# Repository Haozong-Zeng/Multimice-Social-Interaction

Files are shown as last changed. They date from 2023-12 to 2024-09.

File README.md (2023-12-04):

# Multimice-Social-Interaction
This repository contains the codes and documents of the multiple mice social interaction project in Dr. Tim Murphy's Lab at UBC.  
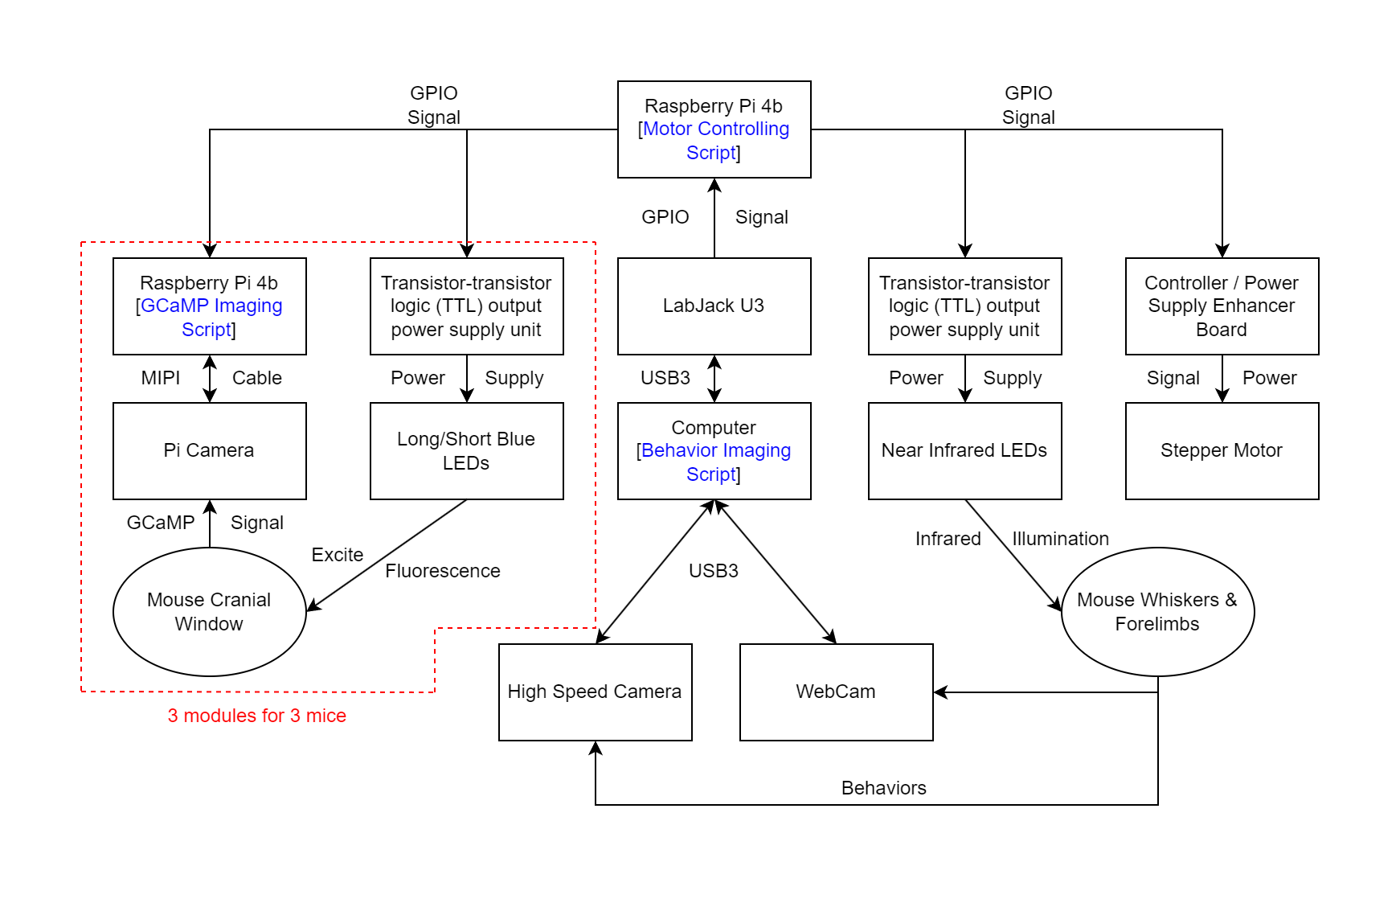
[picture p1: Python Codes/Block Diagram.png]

## Python Codes
This folder contains the python codes for 1) using Raspberry Pi to control the rail system and Pi cameras; 2) controlling the high-speed camera; 3) processing the obtained data. There is also a block diagram explaining how the system works.  
## Hardwares
This folder contains 1) a table with all of the parts; 2) CAD files for the customized parts made by 3D printing or CNC; 3) assembly diagrams to show how the rig is constructed.

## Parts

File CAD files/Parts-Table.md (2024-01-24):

# Parts Required for Constructing the Rig
This table contains a list of parts required to build the experimental setup. These parts are divided into those that can be purchased and those that need to be customized. Customized parts can be obtained by simply providing CAD files to 3D printing and CNC manufacturers, and the processing costs are not high.  
## Parts to be purchased
**1**. 4 Raspberry Pi 4b - Connecting to Pi cameras for brain imaging; GPIO for synchronization, controlling the stepper motor & LEDs. Other versions of Raspberry Pi might require extra modification.  
**2**. 1 LabJack LabJack U3-LV - Connection to a computer with the high-speed camera (OMRON STC-MBS43U3V) to provide GPIO for synchronization.  
**3**. 1 OMRON STC-MBS43U3V camera - Recording whisker movements at high fps.  
**4**. 1 Full-band Beam Splitter (Reflection/Transmission Ratio 80%/20%) from Edmund Optics - Recording whisker & limbs.  
**5**. 1 Computer - Recording behavior data at high fps.  
**6**. 3 Raspberry Pi Cameras (OmniVision OV5647 CMOS sensor) - Recording GCaMP images.  
**7**. 3 MIPI cables - Connecting the camera to Raspberry Pi.  
**8**. 3 Triple-bandpass filters (Chroma 69013m) - One for each GCaMP imaging camera for signal correction.  
**9**. 3 Short blue, 447.5nm Royal Blue Luxeon Rebel LED SP-01-V4 with Thorlabs FB 440-10 nm band pass filters - Providing information about hemodynamic changes.  
**10**. 3 Long blue, 470nm Luxeon Rebel LED SP-01-B6 with Chroma 480/30nm band pass filters - Triggering GCaMP fluorescence.  
**11**. 2 Fosa 140 LED Waterproof Infrared Night Vision Lights - For behavior recording, photoresistor needs to be replaced or shielded.  
**12**. 4 Transistor-transistor logic (TTL) output power supply units - Synchronously turning on the LEDs with GPIO signals.  
**13**. 1 30fps Webcam (HBV‑W202012HD) - Recording forelimbs and torso movements.  
**14**. 1 Stepper Motor  
**15**. 1 Motor Driven Industrial Slide Rail with Supports (Mei Ke Chuan Dong) - Manipulating the positions of the mice.  
**16**. Various Optic Posts, Post Clamps, Optic Breadboards - Flexible, check CAD files for more details.  
## Parts to be customized
**1**. 3 Pi Camera Holders - Holding the GCaMP imaging Pi cameras; 3D printing.  
**2**. 6 Head-fixing Clamps & Bars - Head-fixing the mice; CNC or other metal processing.  
**3**. 3 Transparent Acrylic Tubes - Head-fixing the mice; any mechanical processing that works.  
**4**. 3 Bases that holds the Tubes - Head-fixing the mice; 3D printing.  
**5**. 1 Beam Splitter Holder - Holding the beam splitter; 3D printing.  
**6**. 1 Whisker Imaging Background - A board providing white background for better imaging quality and easier whisker tracking.  
**7**. 2 Flexible Rail Adaptors - Fixing the Mouse Tube or other structure on the rail, allowing some spacial adjustments.

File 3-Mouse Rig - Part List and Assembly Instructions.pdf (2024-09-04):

## DOCUMENTATION FOR 3-MOUSE INTERACTION RIG Total Cost ~ $ 8916 USD

Note: Some costs are approximations or subject to change over time. There may be variations when attempting to reproduce.

## LED LIGHT GUIDE PART LIST

### Bought Parts

Manufacturer | Name | Part ID | Quantity | Cost | Sub-Total
Thorlabs | Liquid Light Guide, Ø3 mm Core, 340 - 800 nm, 4' (1.2 m) Length | LLG03-4H (https://www.thorlabs.com/thorproduct.cfm?partnumber=LLG03-4H) | 3 | $418.14 | $1254.42
Thorlabs | SM1 Lens Tube, 3.00" Thread Depth, One Retaining Ring Included | SM1L30 (https://www.thorlabs.com/thorproduct.cfm?partnumber=SM1L30) | 6 | $29.23 | $175.38
Thorlabs | SM1 Lens Tube, 2.00" Thread Depth, One Retaining Ring Included | SM1L20 (https://www.thorlabs.com/thorproduct.cfm?partnumber=SM1L20) | 3 | $17.85 | $53.55
Thorlabs | SM1 Lens Tube, 1.00" Thread Depth, One Retaining Ring Included | SM1L10 (https://www.thorlabs.com/thorproduct.cfm?partnumber=SM1L10) | 3 | $15.41 | $46.23
Thorlabs | SM1 Lens Tube, 0.50" Thread Depth, One Retaining Ring Included | SM1L05 (https://www.thorlabs.com/thorproduct.cfm?partnumber=SM1L05) | 6 | $13.62 | $81.72
Thorlabs | f=30.0 mm, Ø1" Achromatic Doublet, ARC: 400-700 nm | AC254-030-A (https://www.thorlabs.com/thorproduct.cfm?partnumber=AC254-030-A) | 3 | $96.22 | $288.66
Thorlabs | N-BK7 Bi-Convex Lens, Ø1", f = 25.4 mm, Uncoated | LB1761 (https://www.thorlabs.com/thorproduct.cfm?partnumber=LB1761) | 6 | $30.17 | $181.02
Thorlabs | Ø3 mm LLG to SM1 Adapter | AD3LLG (https://www.thorlabs.com/thorproduct.cfm?partnumber=AD3LLG) | 3 | $38.32 | $114.96
Thorlabs | 30 mm Cage Cube with Dichroic Filter Mount | CM1-DCH (https://www.thorlabs.com/thorproduct.cfm?partnumber=CM1-DCH) | 6 | $192.44 | $1154.64
Thorlabs | Cage Cube Connector for Compact 30 mm Cage Cubes | CM1-CC (https://www.thorlabs.com/thorproduct.cfm?partnumber=CM1-CC) | 3 | $53.47 | $160.41
Thorlabs | 25 mm x 36 mm Longpass Dichroic Mirror, 550 nm Cut-On | DMLP550R (https://www.thorlabs.com/thorproduct.cfm?partnumber=DMLP550R) | 3 | $279.16 | $837.48

Thorlabs | Hard-Coated Bandpass Filter, Ø25 mm, CWL = 440 nm, FWHM = 10 nm | FBH440-10 (https://www.thorlabs.com/thorproduct.cfm?partnumber=FBH440-10) | 3 | $164.67 | $494.01
Thorlabs | SM1 Retaining Ring for Ø1" Lens Tubes and Mounts, 10 Pack | SM1RR-P10 (https://www.thorlabs.com/thorproduct.cfm?partnumber=SM1RR-P10) | 1 | $43.81 | $43.81
Chroma | Dichroic Filter, 455 nm, Size: 26 * 38 mm | AT455DC (https://www.chroma.com/products/parts/at455dc#legend-selector1) | 3 | $175.00 | $525.00
Chroma | Bandpass Filter, 480 nm, Size: 25mmR R=Mounted in Ring | ET480/30x (https://www.chroma.com/products/parts/et480-30x) | 3 | $365.00 | $1095.00
Luxeonstar | Royal-Blue (448 nm) Rebel LED on a SinkPAD-II 20mm Star Base – 1030 mW @ 700mA | SP-01-V4 (https://luxeonstar.com/product/sp-01-v4/) | 3 | $8.33 | $24.99
Luxeonstar | Blue (470 nm) Rebel LED on a SinkPAD-II 10mm Square Base - 65 lm @ 700mA | SP-05-B4 (https://luxeonstar.com/product/sp-05-b4/) | 3 | $10.18 | $30.54
TOTAL | | | | | $6561.83

### Customized Parts

Name | File Name | Quantity | Method
LED Mount Top | Milled as-1.50_2_v2.STL | 6 | Machined
LED Mount Spacer | Spacer_with_wire_hole_as-.500_v2. STL | 6 | Machined
LED Mount Bottom | LED_mount_as-1.50_v2.STL | 6 | Machined

## RIG PART LIST

### Bought Parts

Manufacturer | Name | Part ID | Quantity | Cost | Sub-Total
N/A | ¼-20 Set Screws, Bolts, Nuts, Washers; M2 Screws, Nuts | N/A | Enough | N/A | N/A
N/A | 1.5 Inch Outer Diameter 1⅛ Inch Inner Diameter Acrylic Tubing | N/A | 12 Inch Length | N/A | N/A

Thorlabs | Clamping Fork, 1.24" Counterbored Slot, Universal | CF125 (https://www.thorlabs.com/thorproduct.cfm?partnumber=CF125#ad-image-0) | 2 | $9.68 | $19.36
Thorlabs | Ø1/2" Optical Post, SS, 8-32 Setscrew, 1/4"-20 Tap, L = 4", 5 Pack | TR4-P5 (https://www.thorlabs.com/thorproduct.cfm?partnumber=TR4-P5) | 1 | $30.00 | $30.00
Thorlabs | Ø1/2" Optical Post, SS, 8-32 Setscrew, 1/4"-20 Tap, L = 3" | TR3 (https://www.thorlabs.com/thorproduct.cfm?partnumber=TR3) | 3 | $5.65 | $16.95
Edmund Optics | 6" Length, 8-32 Stud, Steel Post | #58-966 (https://www.edmundoptics.ca/p/6quot-length-8-32-stud-steel-post/15714/) | 2 | $12.50 | $25.00
Edmund Optics | 12" x 12", Breadboard | #53-830 (https://www.edmundoptics.ca/p/12quot-x-12quot-breadboard/10837/) | 2 | $189.00 | $378.00
Edmund Optics | 4" Length, ¼-20 Thread, Post Holder | #58-980 (https://www.edmundoptics.ca/p/4quot-length-frac14-20-thread-post-holder/15728/) | 1 | $15.50 | $15.50
Edmund Optics | 12.7mm - 12.7mm (Fixed), Right Angle Post Clamp | #53-357 (https://www.edmundoptics.ca/p/127mm-127mm-fixed-right-angle-post-clamp/10735/) | 3 | $26.60 | $79.80
Edmund Optics | 12.7mm - 12.7mm (Rotatable), Right Angle Post Clamp | #58-994 (https://www.edmundoptics.ca/p/127mm-127mm-rotatable-right-angle-post-clamp/15738/) | 6 | $31.00 | $186.00
Edmund Optics | 50 x 50mm 80R/20T, VIS Plate Full-Band Beamsplitter | #68-429 (https://www.edmundoptics.ca/p/50-x-50mm-80r20t-vis-plate-beamsplitter/23071/) | 1 | $274.00 | $274.00
Siskiyou | AS-.500 Aluminium Spacer 0.5 Inches Package of 4 (1 Inch diameter) | 60400000E (https://siskiyou.com/as-series-spacer/) | 3 | $22.00 | $66.00
Siskiyou | AS-2.00 Aluminium Spacer 2 Inches Package of 4 (1 Inch diameter) | 60430000E (https://siskiyou.com/as-series-spacer/) | 3 | $32.00 | $96.00
Siskiyou | AS-.250 Aluminium Spacer 2 Inches Package of 4 (1 Inch diameter) | 60390000E (https://siskiyou.com/as-series-spacer/) | 2 | $19.00 | $38.00
Raspberry Pi / PiShop | Flex Cable for Raspberry Pi Camera - 1 meter | 471 (https://www.pishop.ca/product/flex-cable-for-raspberry-pi-camera-1-meter/) | 3 | $3.61 | $10.83
Taobao (Meike Chuandong) | Motor Driven Industrial Slide Rail with Supports (2 attached platforms) | ZH4920 (https://item.taobao.com/item.htm?id=682359959022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) | 1 | ~ $188.17 | ~ $188.17
TOTAL | | | | | ~ $1423.61

### Electronics

Manufacturer | Name | Part ID | Quantity | Cost | Sub-Total
RaspberryPi / PiShop | Raspberry Pi Model 4b (8 GB RAM) | 8GB-9006 (https://www.pishop.ca/product/raspberry-pi-4-model-b-8gb/?src=raspberrypi) | 4 | $76.51 | $306.04
Waveshare | RPi Camera (B), Adjustable-Focus | RPi Camera (B) (https://www.waveshare.com/rpi-camera-b.htm) | 3 | $15.99 | $47.97
Aegis Electronic | Omron USB3 Vision CMOS Camera, 0.4 MP, Monochrome, Cased | STC-MBS43U 3V (https://aegis-elec.com/sentech-stc-mbs43u3v-stcmbs43u3v-usb3-vision-cmos-0-4-mp-monochrome-cased.html) | 1 | $395.13 | $395.13
Amazon/Best Buy | 30fps Webcam (HBV‑W202012HD) | N/A | 1 | ~ $11.00 | ~ $11.00
Amazon | Fosa 140 LED Waterproof Infrared Night Vision Light | N/A | 2 | ~ $14.60 | ~ $29.20
LabJack | LabJack U3-LV | LabJack U3-LV (https://labjack.com/products/u3) | 1 | $116.64 | $116.64
Sparkfun | Stepper Motor - 125 oz.in (200 steps/rev, 600mm Wire) | ROB-13656 (https://www.sparkfun.com/products/13656) | 1 | $24.42 | $24.42
N/A | LED Driver | N/A | 4 | N/A | N/A
N/A | Transistor-transistor logic (TTL) output power supply unit | N/A | 4 | N/A | N/A
N/A | Computer | N/A | 1 | N/A | N/A
TOTAL | | | | | ~ $930.40

### Customized Parts

Name | File Name | Quantity | Method
Pi Camera Holders | pi-camera-holder_v2L.stl OR pi-camera-holder_v2R.stl | 3 | 3D Printing
Head-fixing Clamps | Head-fixing Clamp.STEP | 6 | CNC or other metal processing
Head-fixing Bars | Head-fixing Bar.STEP | 6 | CNC or other metal processing
Transparent Acrylic Tubes | Acrylic_Tube_Mockup.STL Cut a 3 ¾ inch length of tubing, then remove the top half starting from one end to ¾ of an inch into the tube. | 3 | Any clean cutting method

Tube-Holding Base | mouse-tube-holder_imperial_modified.stl | 3 | 3D Printing
Beam Splitter Holder | beamsplitter_behavior.stl | 1 | 3D Printing
Whisker Imaging Background | N/A | 1 | Any white board/background works
Flexible Rail Adaptors | rail_flexible_adaptor.stl | 2 | Any mechanical processing
Rail Mockup | rail.STEP | 1 | Virtual Mockup Only

## LED LIGHT GUIDE ASSEMBLY

1) Insert the 550 nm longpass dichroic mirror and 455 nm dichroic mirror into cage cubes
2) On the top face of the 550 nm cage cube, attach in order:
a) 0.50’’ Lens Tube
b) 480 nm Bandpass Filter
c) 3.00’’ Lens Tube
d) Bi-Convex Lens
e) 470 nm Blue LED (attached to LED mount)
3) On the top face of the 455 nm cage cube, attach in order:
a) 1.00’’ Lens Tube
b) 0.50’’ Lens Tube
c) 440 nm Bandpass Filter
d) 3.00’’ Lens Tube
e) Bi-Convex Lens
f) 448 nm Royal Blue LED (attached to LED mount)
4) Connect both cage cubes together using the connector
5) On the other side of the 455 nm cage cube, attach in order:
a) 2.00’’ Lens Tube
b) Achromatic Doublet
c) Liquid Light Guide Adapter
d) Liquid Light Guide

Repeat these instructions to build 3 LED Light Guides, one for each mouse in the interaction rig.

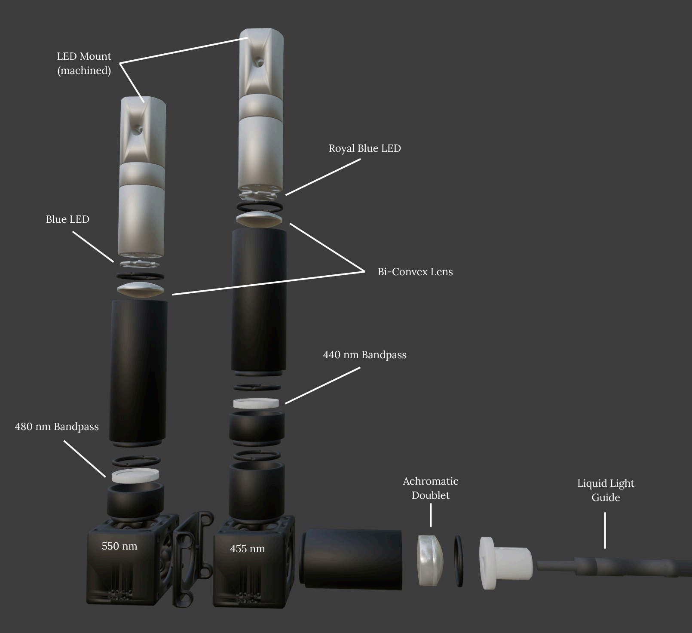
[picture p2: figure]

Figure 1. Liquid Light Guide Setup

## RIG ASSEMBLY

1) Attach the rail system securely down onto a surface.
2) Screw a tube-holding base onto each sliding platform on the rails, and fix them 50 cm apart (25 cm away from the center).

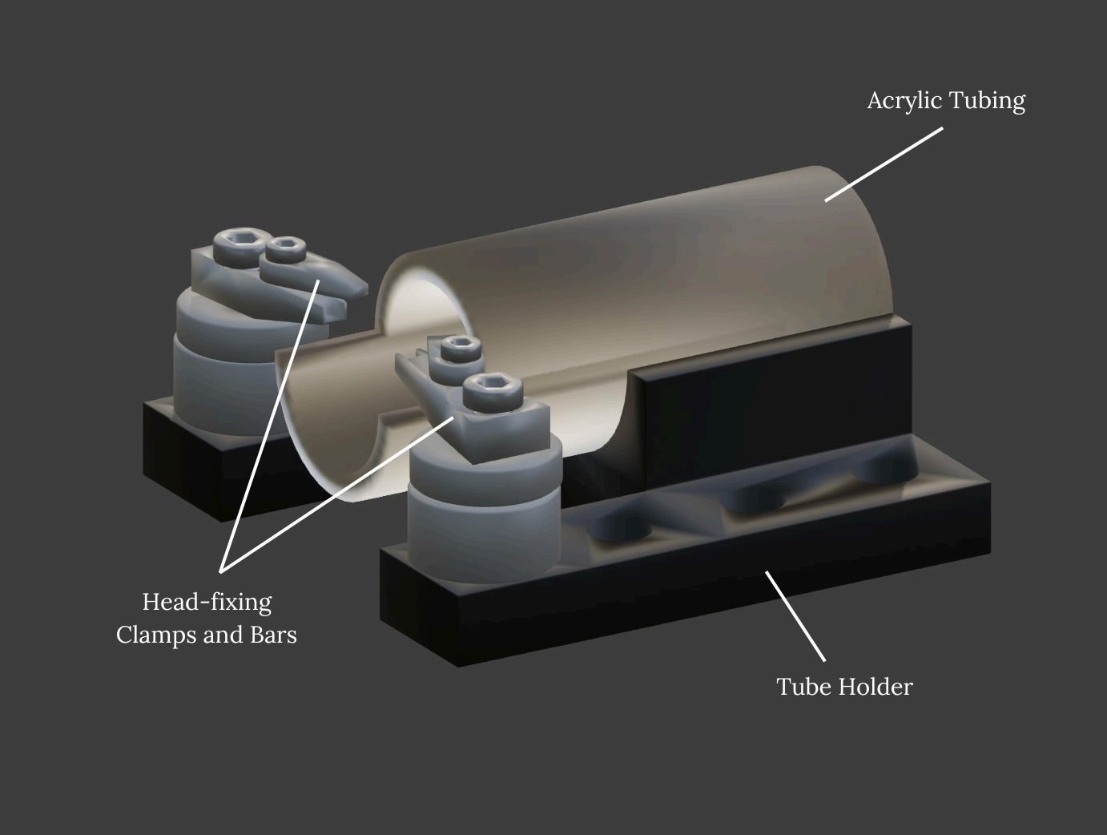
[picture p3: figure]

Figure 2. Mouse Tube Setup (Step 3)

3) Do the following for each tube-holder:
a) Superglue the cut acrylic tubing into the holder with the open side of the tube coinciding with the longer edges of the base.
b) Screw a 0.50 inch spacer and 0.25 inch spacer onto the last hole on both sides of the base.
c) Onto each spacer stack, attach a head-fixing clamp and then a head-fixing bar on top. The clamps should be positioned towards the open end of the tube.

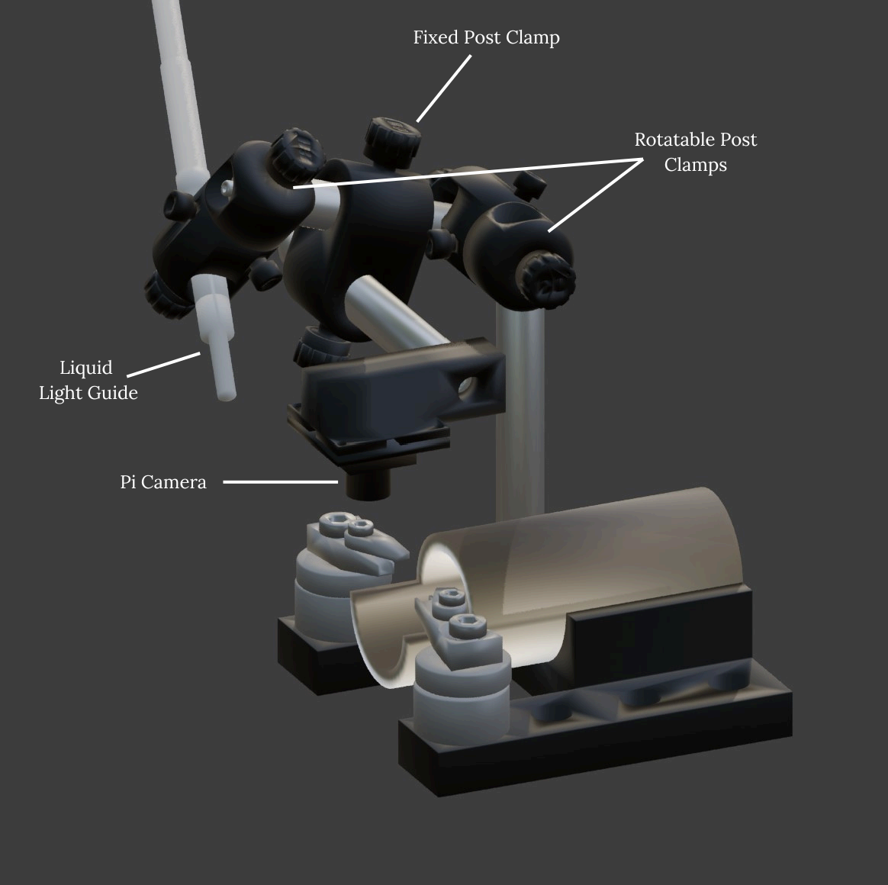
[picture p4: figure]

Figure 3. Mouse Platform Setup on Rail (Step 4)

4) For each rail platform:
a) Screw a 4’’ post on one side of the tube and place a rotatable right angle post clamp on the end.
b) Through the other opening on the clamp, parallel to the tubing, insert a 3’’ inch post. Slide a fixed right angle post clamp onto the middle of the post and another rotatable right angle clamp onto the end.
c) Slide one end of a Liquid Light Guide into the rotatable right angle clamp and ensure that it is pointing towards the area where the mouse window would be.
d) Insert a 4’’ post through the unoccupied hole of the fixed right angle clamp and on the other end, place a pi camera holder equipped with a pi camera. The pi camera should point towards the tube opening.

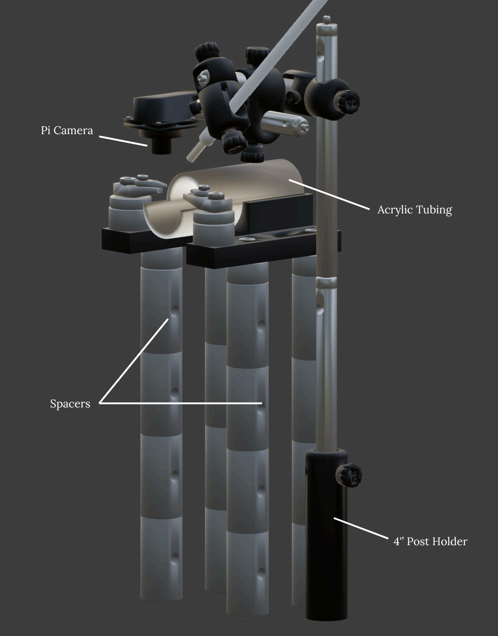
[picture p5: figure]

Figure 4. Mouse Platform Setup on Tower (Steps 5-7)

5) Using 2 inch and 0.5 inch spacers, build a 4-corner tower platform behind the center of the rail to hold the final tube holder at equal height to those on the rail. When mice are in the tubes, there should be about 6-12 mm of space between the snouts of those on the rail and tower. Clamping forks can be used to ensure tower legs remain stable.
6) Next to the towered platform, place a 4’’ post holder and stabilize it with a clamping fork. Insert two 6’’ posts, then place a rotatable right angle clamp 1 inch from the end.
7) Repeat steps 4b to 4d for the final platform.

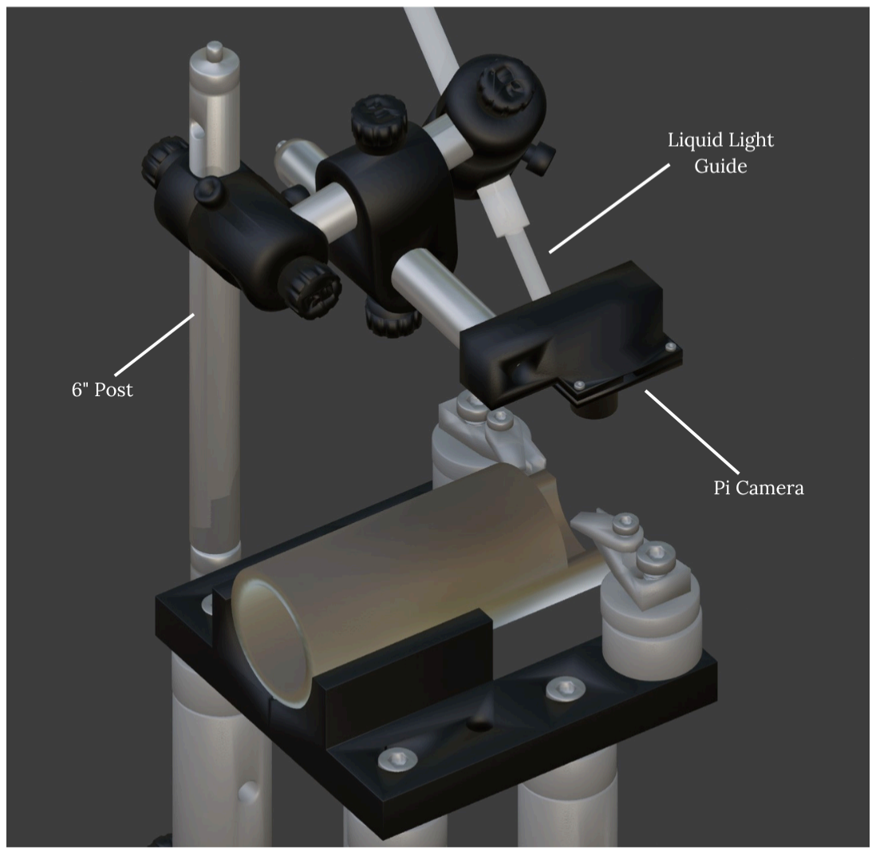
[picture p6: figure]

Figure 5. Mouse Platform Setup on Tower, Back, Zoomed In (Steps 6-7)

8) Use MIPI cables to attach each pi camera to an individual Raspberry Pi unit.
9) Underneath the stationary mouse, between the tower platform and the rail, place an HD camera to record mouse limb movement. This should sit in the bottom slot of the 3D printed beamsplitter holder, pointed up to where the beam splitter is inserted.
10) Bracket the HD camera with two infrared lights to illuminate the interaction area. Adjust height using spacers as necessary.
11) Place a high speed camera pointed towards the illumination area to record whisker movement.
12) Attach a stepper motor to the rig and connect it to a driver.
13) Have a fourth Raspberry Pi unit connect to the stepper motor and LED drivers to act as a control center for rig movement and lighting.

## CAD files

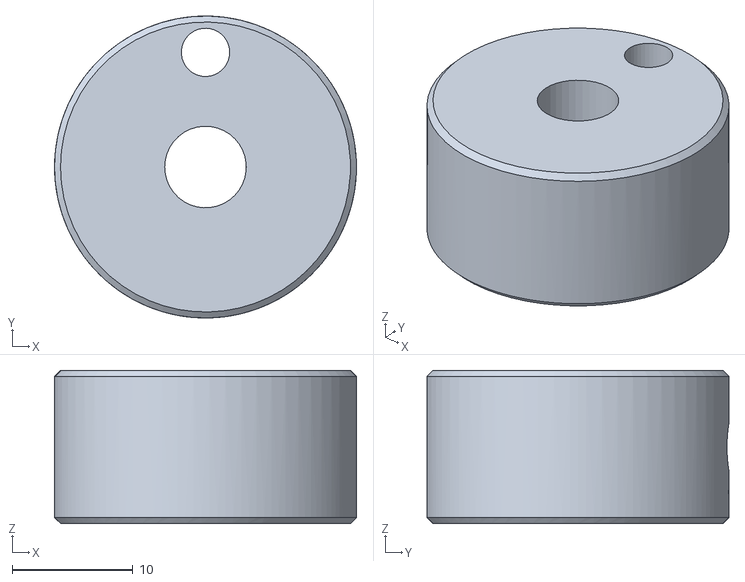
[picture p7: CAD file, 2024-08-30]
CAD files/Spacer_with_wire_hole_as-.500_v2.STL
25.0 x 25.0 x 12.7

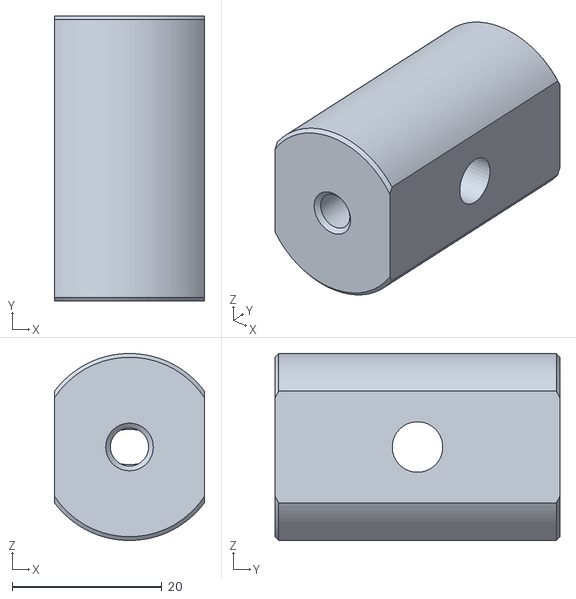
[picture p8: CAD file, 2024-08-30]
CAD files/Milled_as-1.50_2_v2.STL
20.1 x 38.1 x 25.0

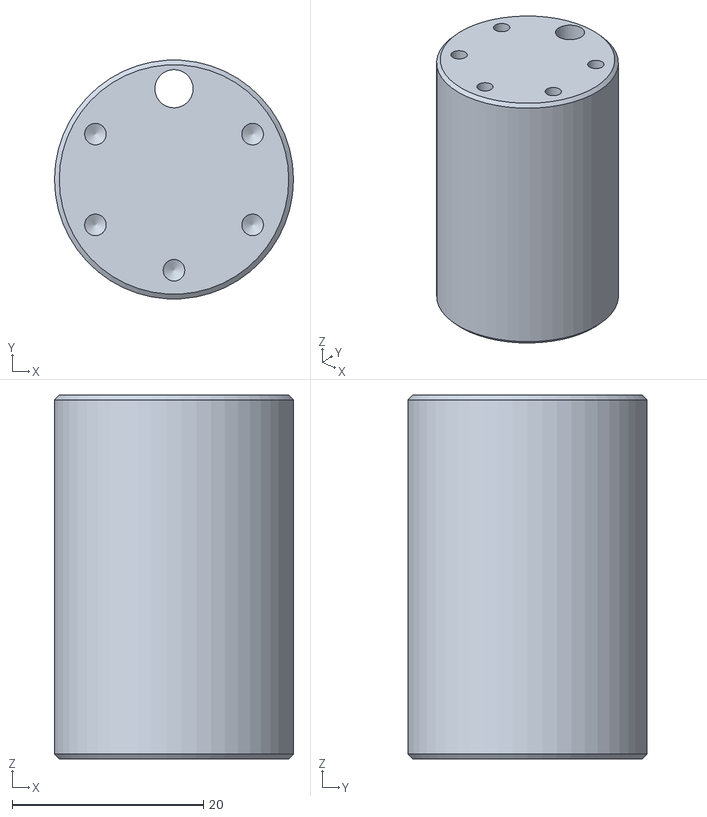
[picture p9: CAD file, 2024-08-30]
CAD files/LED_mount_as-1.50_v2.STL
25.0 x 25.0 x 38.1

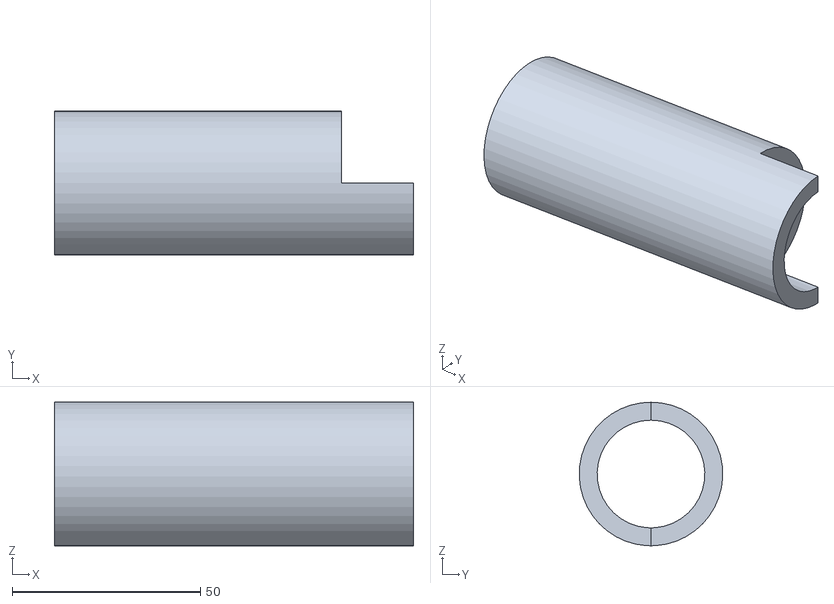
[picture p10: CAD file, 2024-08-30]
CAD files/Acrylic_Tube_Mockup.STL
95.2 x 38.1 x 38.1

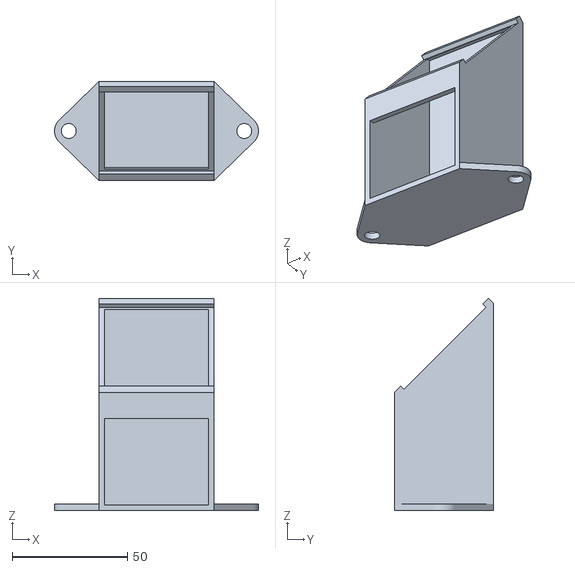
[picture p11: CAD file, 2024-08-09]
CAD files/beamsplitter_behavior.stl
88.6 x 43.0 x 92.2

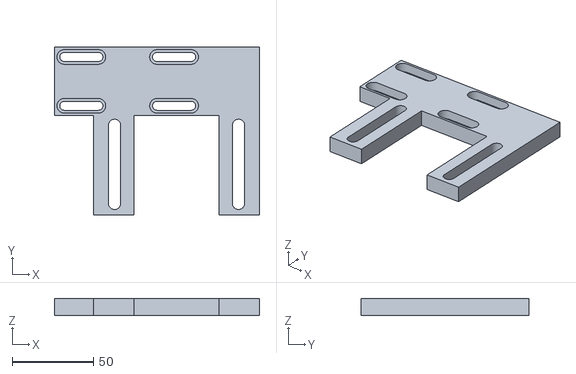
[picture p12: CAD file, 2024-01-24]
CAD files/rail_flexible_adaptor.stl
126.0 x 103.0 x 10.5

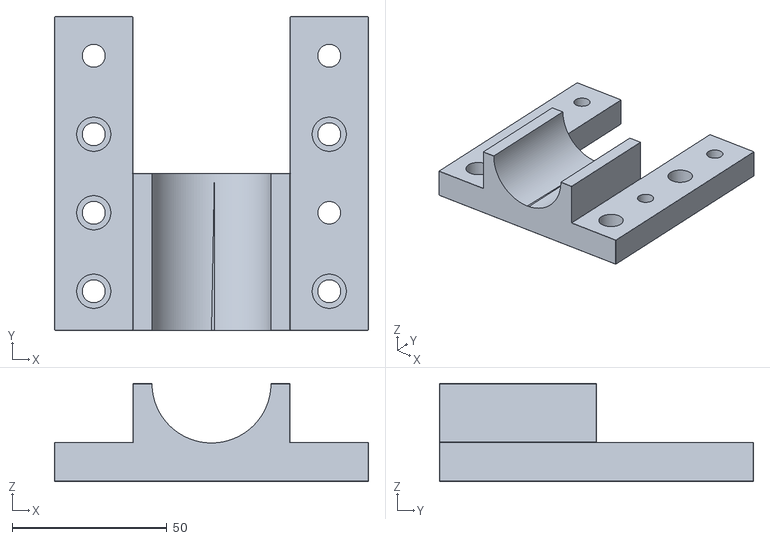
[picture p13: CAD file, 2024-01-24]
CAD files/mouse-tube-holder_imperial_modified.stl
101.6 x 101.6 x 31.8

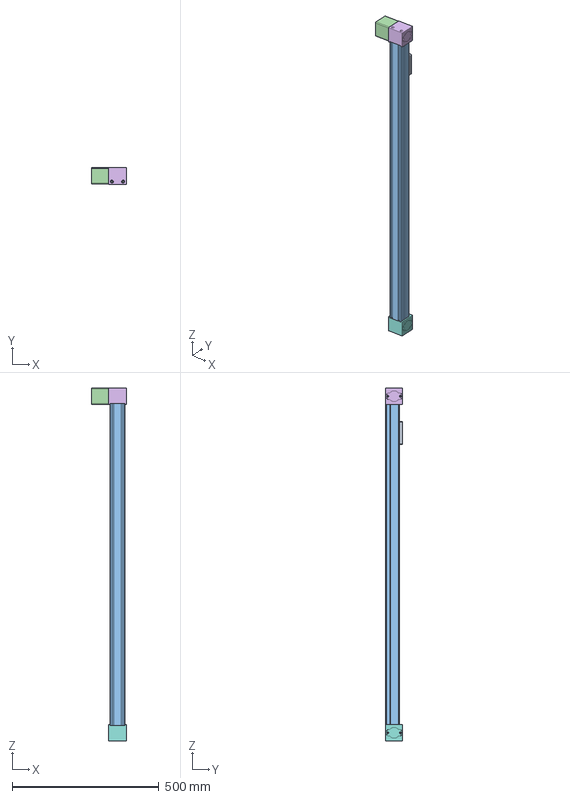
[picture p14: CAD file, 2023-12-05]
CAD files/rail.STEP
118.0 x 59.1 x 1202.1 mm
XF50-1000ѐ³
XF50-1000ѐ³001
XF50-1000ѐ³002
XF50-1000ѐ³003
XF50-1000ѐ³004
XF50-1000ѐ³005
XF50-1000ѐ³006
XF50-1000ѐ³007
XF50-1000ѐ³008
XF50-1000ѐ³009
XF50-1000ѐ³010
XF50-1000ѐ³011
XF50-1000ѐ³012
XF50-1000ѐ³013
XF50-1000ѐ³014

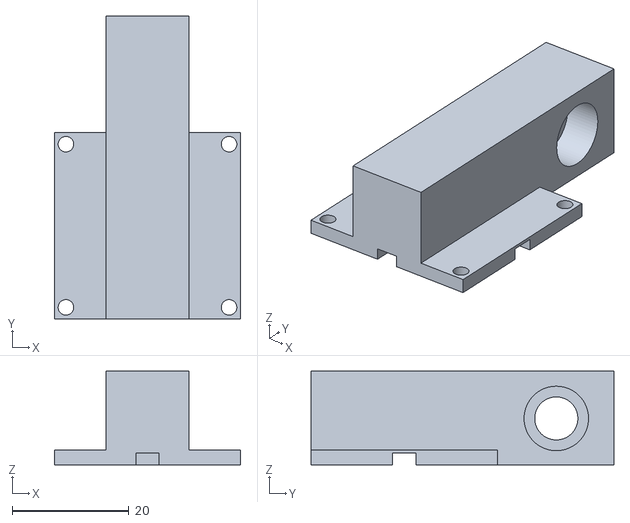
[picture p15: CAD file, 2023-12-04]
CAD files/pi-camera-holder_v2R.stl
32.0 x 52.0 x 16.0

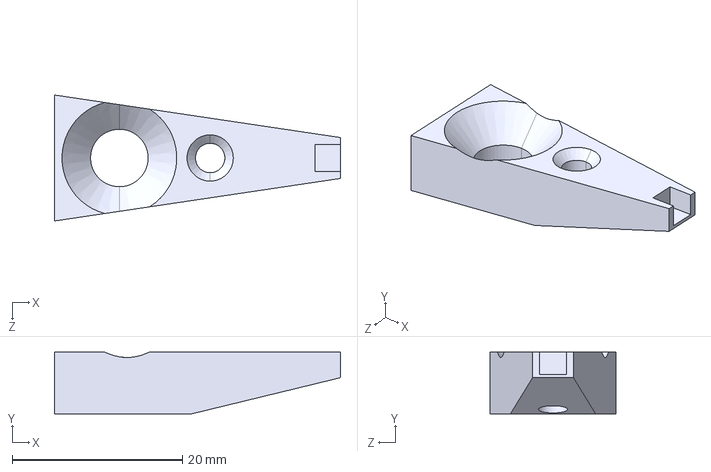
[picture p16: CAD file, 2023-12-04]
CAD files/Head-fixing Clamp.STEP
33.6 x 7.25 x 14.8 mm

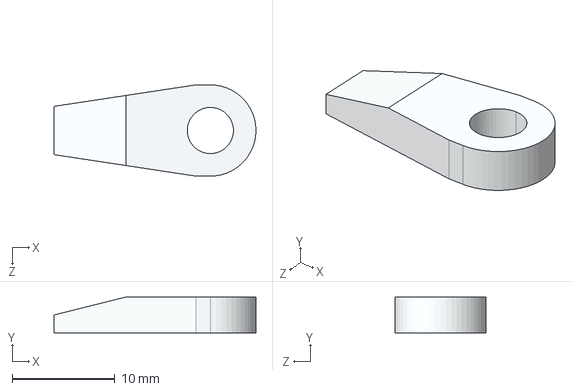
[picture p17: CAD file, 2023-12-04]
CAD files/Head-fixing Bar.STEP
19.7 x 3.50 x 8.89 mm

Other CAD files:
CAD files/pi-camera-holder_v2L.stl

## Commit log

2023-12-04 Python scripts for high speed camera with LabJack
2023-12-04 Metal bar for head-fixing the mouse, part of the whole clamp
    [Head-fixing Bar.STEP]
2023-12-04 Pi Camera holder - left, designed by Luis
    [pi-camera-holder_v2L.stl]
2023-12-04 Pi Camera holder - right, designed by Luis
    [pi-camera-holder_v2R.stl]
2023-12-04 Holder for the tube, designed by Luis
    [mouse-tube-holder_imperial_diesel2p.stl]
2023-12-05 The moter driven rail to move the mice
    [rail.STEP]
2024-01-24 Tube holder, imperial, modified for the rail
    [mouse-tube-holder_imperial_modified.stl]
2024-01-24 Flexible adaptor to fit the tube holder
    [rail_flexible_adaptor.stl]
2024-08-09 3D printed part for the beam splitter / camera
    [beamsplitter_behavior.stl]
2024-08-30 Transparent tube for holding a mouse, by Sruthi
    [Acrylic_Tube_Mockup.STL]
2024-08-30 LED mount, by Sruthi
    [LED_mount_as-1.50_v2.STL]
2024-08-30 Spacer, by Sruthi
    [Spacer_with_wire_hole_as-.500_v2.STL]
